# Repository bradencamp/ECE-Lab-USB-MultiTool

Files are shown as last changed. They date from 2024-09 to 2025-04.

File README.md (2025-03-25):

# ECE-Lab-USB-Multitool
In recent years students have been required to purchase USB Laboratory Instruments such as the Analog Discovery 2 (AD2) from Digilent Inc or the Advanced Active Learning Module (ADALM 2000) from Analog Devices. These devices allow the students to complete Laboratory exercises at home and to experiment on their own time without the need to rely on open lab hours. The COVID pandemic created a high demand for such devices as throughout the US lab classes have been converted to at-home labs. This high demand in concert with the chip crises has propelled the price for these devices to currently $199 and $249 (academic price for the AD2 and AD3 respectively) and $237 (ADALM2000).

This USB Multi-function Laboratory Instrument will be inexpensive and therefore less capable than the AD2 or ADALM 2000 while still fulfilling the requirements for most laboratory exercises in the undergraduate ECE curriculum. This new device should use a microcontroller with analog front ends for the Oscilloscope and Wave Form Generator functionality. It should function as a 2 channel Oscilloscope and Arbitrary Waveform Generator (AWG) with a Bandwidth of up to 2 MHz and a sample rate of 5 Msps, a 16 channel logic analyzer, and be controllable via USB from a PC (Windows, Mac, and Linux) as well as offering live waveform viewing on a PC. The total part cost should not exceed $50. A similar project was once offered by the Opencope MZ (https://digilent.com/reference/test-and-measurement/openscope-mz/start) which has been discontinued.

Previous senior design projects have built a one-channel prototype for of the oscilloscope and a two channel AWG. However, the oscilloscope did not fully meet the requirements. The arbitrary waveform generator function is complete. The logic analyzer is now a separate project and currently being designed. The goal of this project is to learn from the oscilloscope prototype and create one that meets the requirements and integrate the arbitrary waveform generator and the logic analyzer, all with an intuitive and easy to use graphical user interface on the PC using PyQtGraph. This project requires analog circuit design of amplifiers, filters, etc., while being cost-conscious. The fewer different parts are needed and the fewer parts are needed overall, the more likely you'll meet the $50 target. It also requires programming of an STM-32 microcontroller in C, GUI design and programming in Python.

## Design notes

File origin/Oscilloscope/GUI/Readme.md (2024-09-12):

# Python libraries needed
- time
- Pyserial
- Serial
- PyQt5
- NumPy
- PyQtGraph
# Instructions

- For the GUI to run, the port and baudrate number needs to match the MCU's serial. 
- The board also needs to be connected for it to work.
- To change the port and baudrate number, change reader = SerialReader(port='COM7', baudrate=12000000) in line 400 of the code.
- COM7 can be changed to COM# depending on the port number in the Device Manager of Windows.
- The main function "def update():" is the main loop that collects the data and plots it.

# Improvments to the code

- Implementing the "time" function as the code is getting the ADC data can be used to set a time function that goes to the x-axis.

- using NumPy's FFT function can be used to show the frequincy number being generated.

- Creating an automatic COM port detector to remove the need of updating it for each new device.

What can suffice is using this example:
```python
	com_number, ok = QtGui.QInputDialog.getText(None, "COM Port", "Enter COM#:")
	if ok:
		ser = serial.Serial(f"COM{com_number}", 12000000)
	else:
		print("Wrong COM port, exiting...")
		exit()
```
This  will prompt a window to input the COM# before opining the GUI.

# FIXME
- add trigger function.

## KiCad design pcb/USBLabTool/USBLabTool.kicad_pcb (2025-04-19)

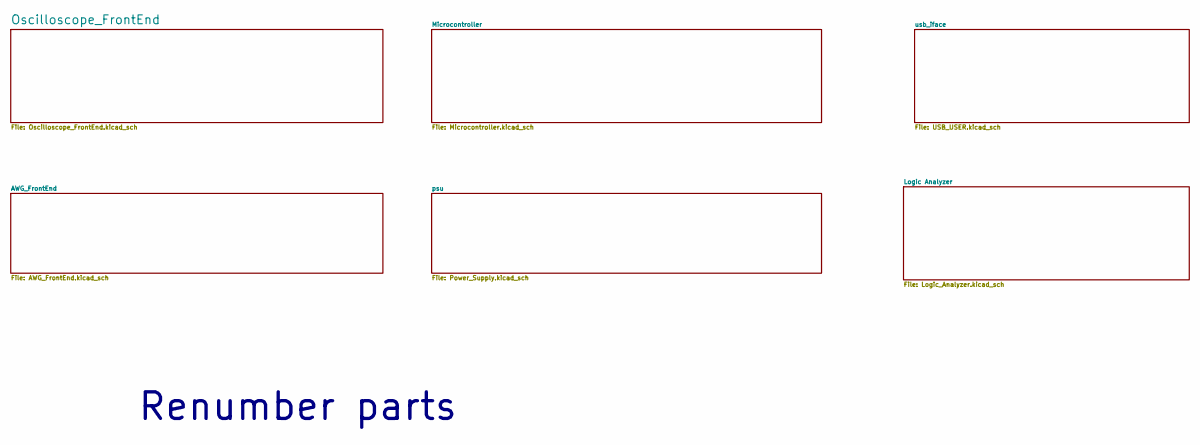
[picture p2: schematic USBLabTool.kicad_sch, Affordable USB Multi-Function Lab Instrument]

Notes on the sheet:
Renumber parts

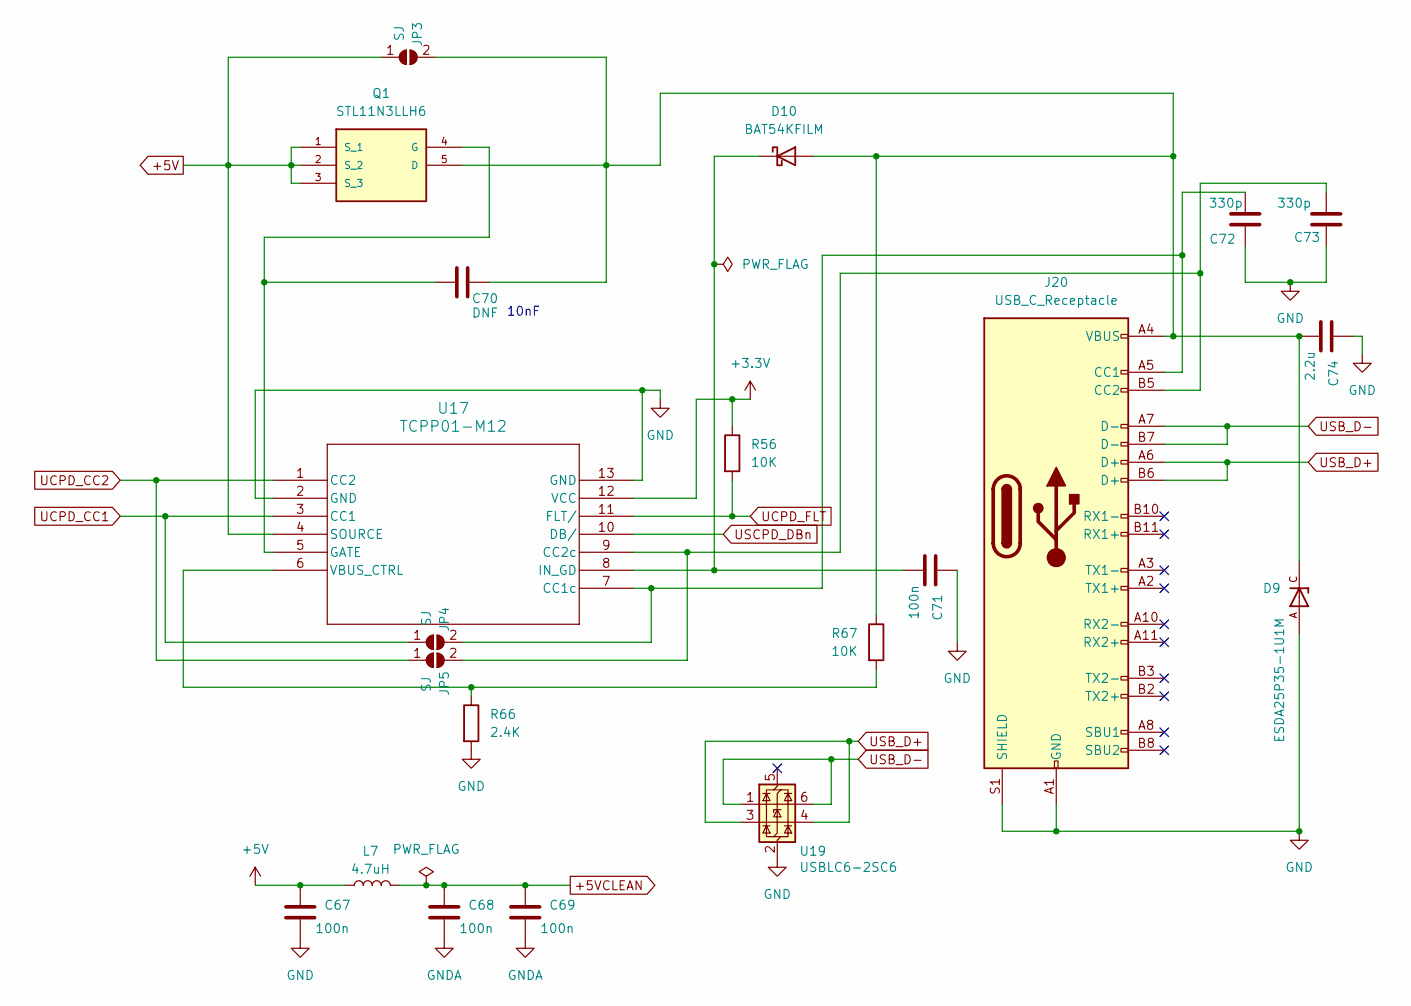
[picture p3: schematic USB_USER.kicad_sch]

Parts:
C67, C68, C69, C71: 100n; C_0603_1608Metric_Pad1.08x0.95mm_HandSolder
C70: DNF; C_0603_1608Metric_Pad1.08x0.95mm_HandSolder
C72, C73: 330p; C_0201_0603Metric_Pad0.64x0.40mm_HandSolder
C74: 2.2u; C_0603_1608Metric_Pad1.08x0.95mm_HandSolder
D9: ESDA25P35-1U1M; TVS_ESDA25P35-1U1M; PARTREV 2
D10: BAT54KFILM; D_SOD-523
J20: USB_C_Receptacle; USB_C_Receptacle_Amphenol_12401610E4-2A
JP3, JP4, JP5: SJ; SolderJumper-2_P1.3mm_Open_RoundedPad1.0x1.5mm
L7: 4.7uH; L_0603_1608Metric_Pad1.05x0.95mm_HandSolder; Mouser REF 80-L0603B470KPWFT
Q1: STL11N3LLH6; STL20N6F7; MANUFACTURER_PART_NUMBER STL11N3LLH6; DigiKey_Part_Number 497-11099-2-ND
R56, R67: 10K; R_0603_1608Metric
R66: 2.4K; R_0603_1608Metric
U17: TCPP01-M12; QFN12_TCPP01-M12_STM
U19: USBLC6-2SC6; SOT-23-6

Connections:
+3.3V: R56.1, U17.12 (VCC); also elsewhere on the board
+5V: C67.1, JP3.1 (A), L7.1, Q1.1 (S_1), Q1.2 (S_2), Q1.3 (S_3), U17.4 (SOURCE); also elsewhere on the board
+5VCLEAN: C68.1, C69.1, L7.2; also elsewhere on the board
GND: C67.2, C71.1, C72.1, C73.1, C74.1, D9.A, J20.A1 (GND), J20.A12 (GND), J20.B1 (GND), J20.B12 (GND), J20.S1 (SHIELD), R66.2, U17.2 (GND), U17.13 (GND), U19.2 (GND); also elsewhere on the board
GNDA: C68.2, C69.2; also elsewhere on the board
unnamed: C70.1, C74.2, D9.C, D10.2 (A), J20.A4 (VBUS), J20.A9 (VBUS), J20.B4 (VBUS), J20.B9 (VBUS), JP3.2 (B), Q1.5 (D), R67.1
unnamed: C71.2, D10.1 (K), U17.8 (IN_GD)
unnamed: C72.2, J20.A5 (CC1), JP4.2 (B), U17.7 (CC1c)
unnamed: C73.2, J20.B5 (CC2), JP5.2 (B), U17.9 (CC2c)
unnamed: C70.2, Q1.4 (G), U17.5 (GATE)
unnamed: R66.1, R67.2, U17.6 (VBUS_CTRL)
UCPD_CC1: JP4.1 (A), U17.3 (CC1); also elsewhere on the board
UCPD_CC2: JP5.1 (A), U17.1 (CC2); also elsewhere on the board
UCPD_FLT: R56.2, U17.11 (FLT/); also elsewhere on the board
USB_D+: J20.A6 (D+), J20.B6 (D+), U19.3 (I/O2), U19.4 (I/O2); also elsewhere on the board
USB_D-: J20.A7 (D-), J20.B7 (D-), U19.1 (I/O1), U19.6 (I/O1); also elsewhere on the board
USCPD_DBn: U17.10 (DB/); also elsewhere on the board

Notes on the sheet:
10nF

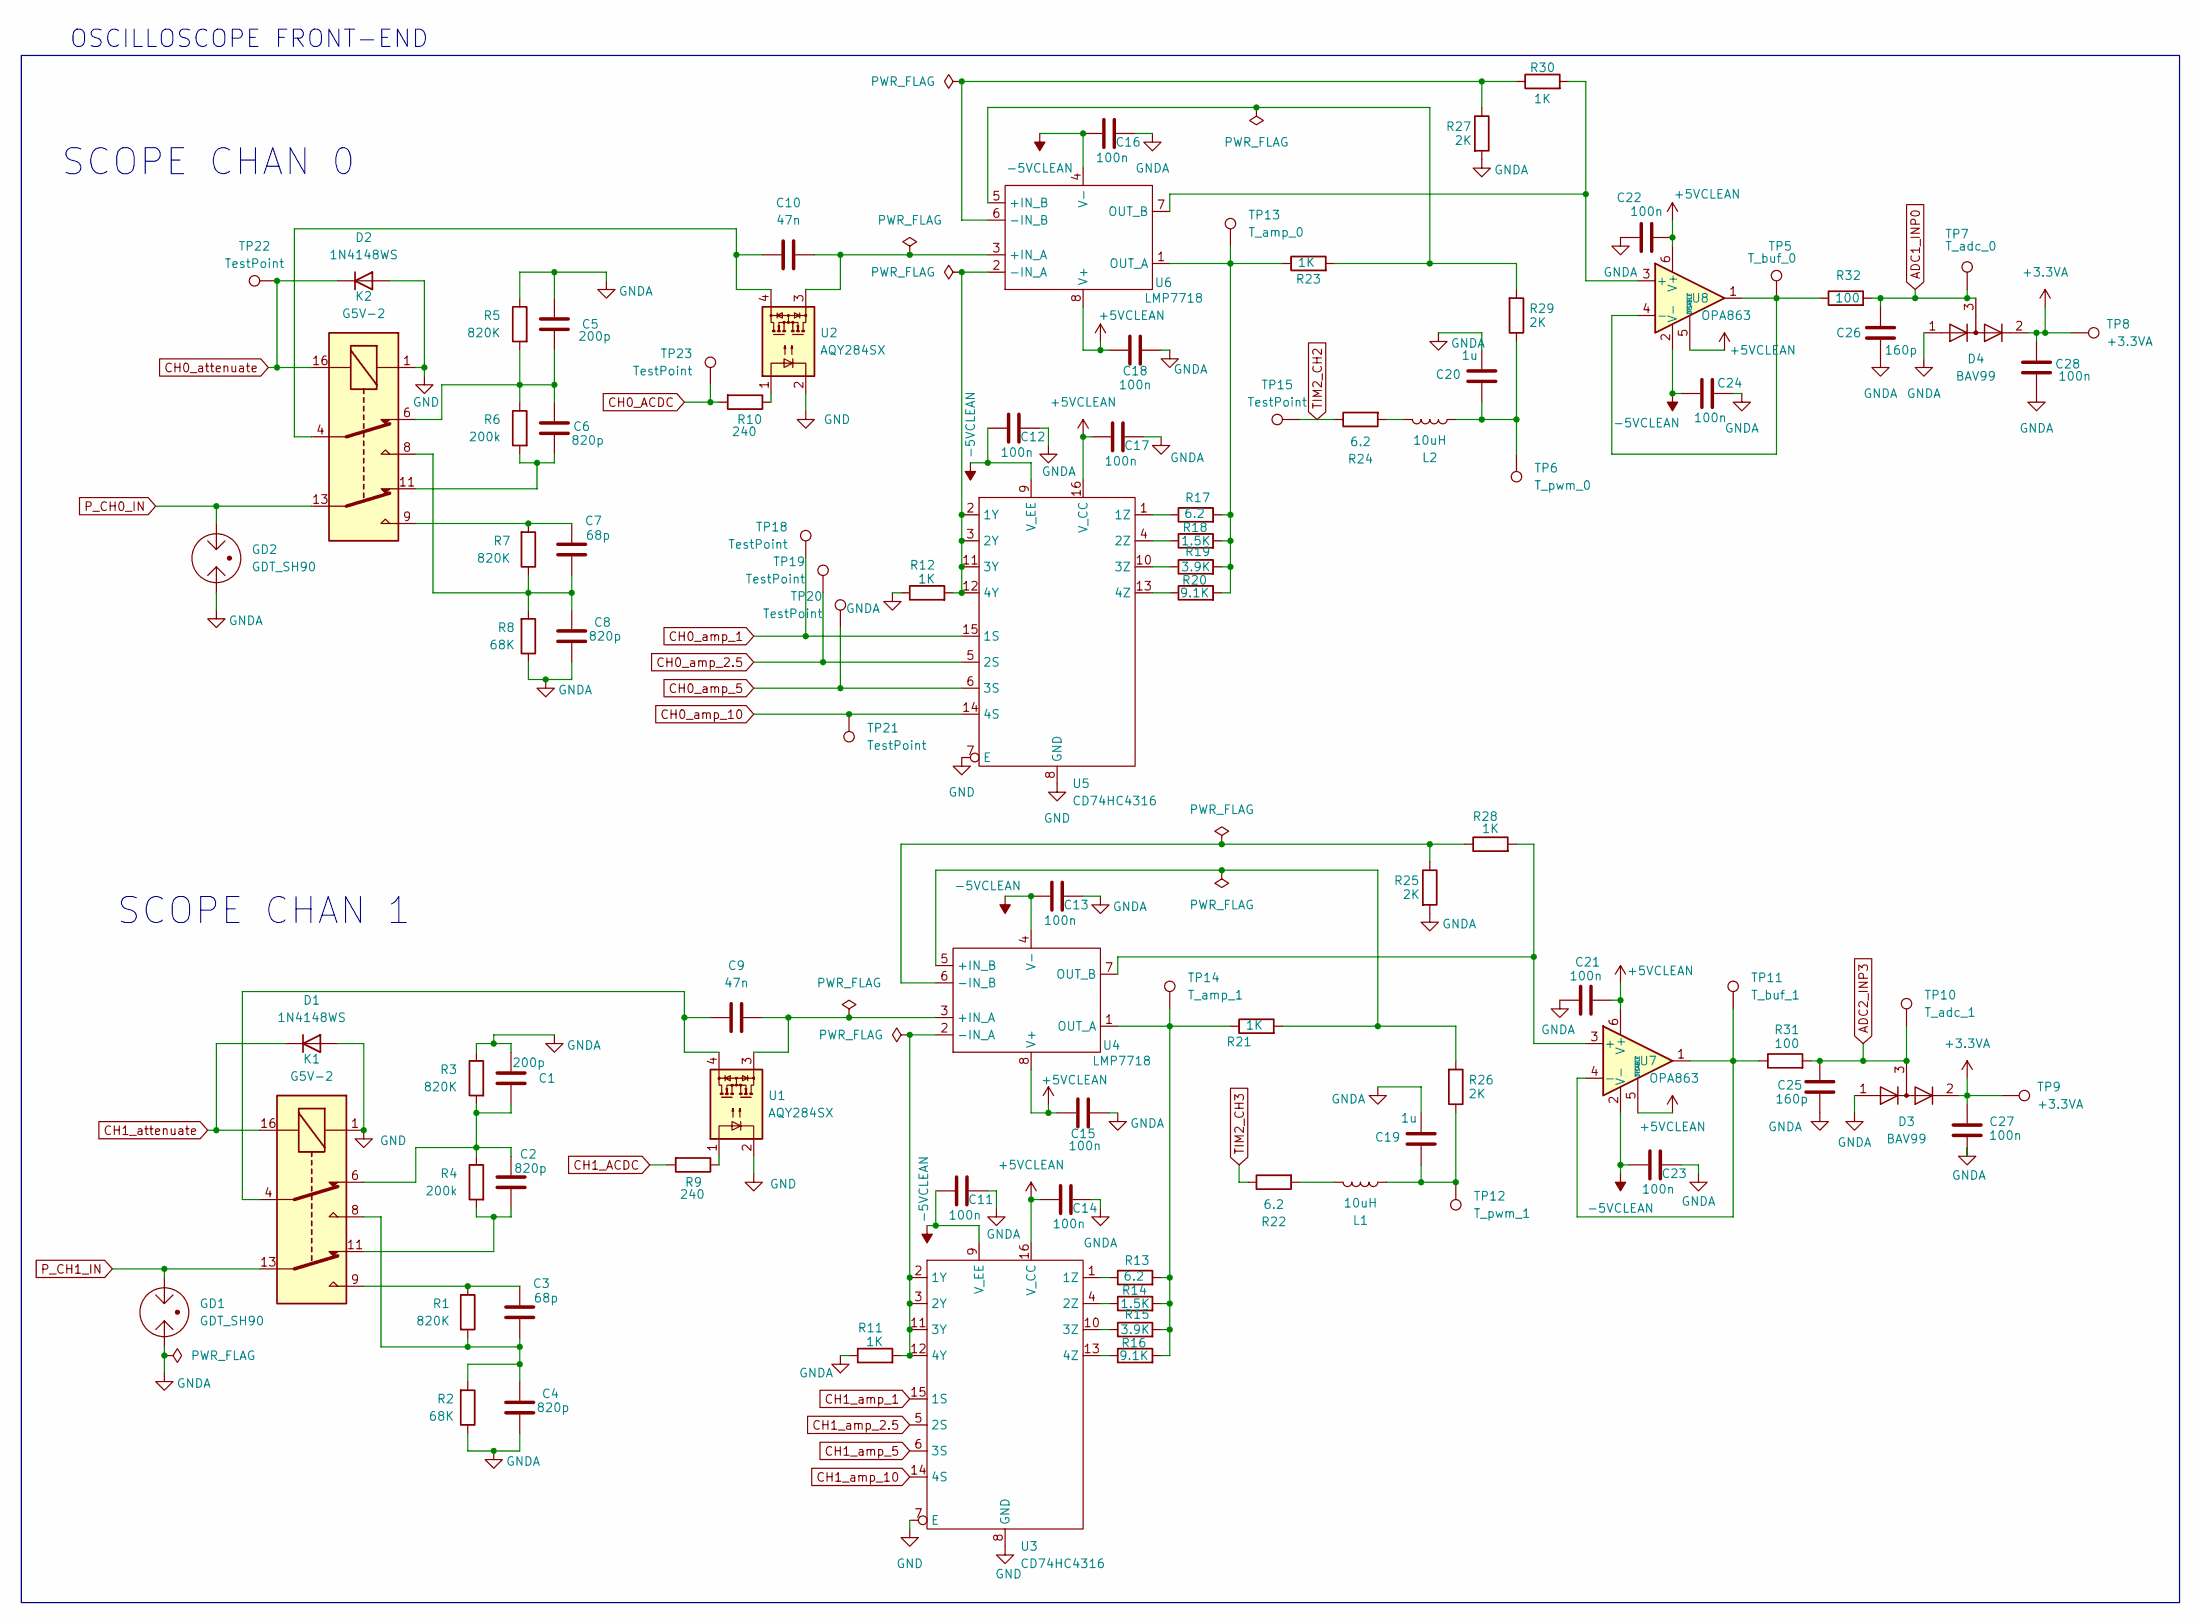
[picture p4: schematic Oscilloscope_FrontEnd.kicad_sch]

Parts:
C1, C5: 200p; C_0603_1608Metric_Pad1.08x0.95mm_HandSolder
C2, C4, C6, C8: 820p; C_0603_1608Metric_Pad1.08x0.95mm_HandSolder
C3, C7: 68p; C_0603_1608Metric_Pad1.08x0.95mm_HandSolder
C9, C10: 47n; C_0603_1608Metric_Pad1.08x0.95mm_HandSolder
C11, C12, C13, C14, C15, C16, C17, C18, C21, C22, C23, C24, C27, C28: 100n; C_0603_1608Metric_Pad1.08x0.95mm_HandSolder
C19, C20: 1u; C_0603_1608Metric_Pad1.08x0.95mm_HandSolder
C25, C26: 160p; C_0603_1608Metric_Pad1.08x0.95mm_HandSolder
D1, D2: 1N4148WS; D_SOD-323
D3, D4: BAV99; SOT-23
GD1, GD2: GDT_SH90; GDT_SH_LTF
K1, K2: G5V-2; Relay_DPDT_Omron_G5V-2
L1, L2: 10uH; L_0603_1608Metric_Pad1.05x0.95mm_HandSolder
R1, R3, R5, R7: 820K; R_0603_1608Metric_Pad0.98x0.95mm_HandSolder
R2, R8: 68K; R_0603_1608Metric_Pad0.98x0.95mm_HandSolder
R4, R6: 200k; R_0603_1608Metric_Pad0.98x0.95mm_HandSolder
R9, R10: 240; R_0603_1608Metric_Pad0.98x0.95mm_HandSolder
R11, R12, R21, R23, R28, R30: 1K; R_0603_1608Metric_Pad0.98x0.95mm_HandSolder
R13, R17, R22, R24: 6.2; R_0603_1608Metric_Pad0.98x0.95mm_HandSolder
R14, R18: 1.5K; R_0603_1608Metric_Pad0.98x0.95mm_HandSolder
R15, R19: 3.9K; R_0603_1608Metric_Pad0.98x0.95mm_HandSolder
R16, R20: 9.1K; R_0603_1608Metric_Pad0.98x0.95mm_HandSolder
R25, R26, R27, R29: 2K; R_0603_1608Metric_Pad0.98x0.95mm_HandSolder
R31, R32: 100; R_0603_1608Metric_Pad0.98x0.95mm_HandSolder
TP5: T_buf_0; TestPoint_Pad_D2.0mm
TP6: T_pwm_0; TestPoint_Pad_D2.0mm
TP7: T_adc_0; TestPoint_Pad_2.0x2.0mm
TP8, TP9: +3.3VA; TestPoint_Pad_D2.0mm
TP10: T_adc_1; TestPoint_Pad_D2.0mm
TP11: T_buf_1; TestPoint_Pad_D2.0mm
TP12: T_pwm_1; TestPoint_Pad_D2.0mm
TP13: T_amp_0; TestPoint_Pad_D2.0mm
TP14: T_amp_1; TestPoint_Pad_D2.0mm
TP15, TP18, TP19, TP20, TP21, TP22, TP23: TestPoint; TestPoint_Pad_2.0x2.0mm
U1, U2: AQY284SX; SOP-4_3.8x4.1mm_P2.54mm
U3, U5: CD74HC4316; TSSOP-16_4.4x5mm_P0.65mm
U4, U6: LMP7718; VSSOP-8_3x3mm_P0.65mm
U7, U8: OPA863; SOT-23-6_Handsoldering

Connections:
+3.3VA: C27.1, C28.1, D3.2 (A), D4.2 (A), TP8.1, TP9.1; also elsewhere on the board
+5VCLEAN: C14.1, C15.1, C17.1, C18.1, C21.2, C22.2, U3.16 (V_CC), U4.8 (V+), U5.16 (V_CC), U6.8 (V+), U7.5 (~DISABLE), U7.6 (V+), U8.5 (~DISABLE), U8.6 (V+); also elsewhere on the board
-5VCLEAN: C11.1, C12.1, C13.1, C16.1, C23.1, C24.1, U3.9 (V_EE), U4.4 (V-), U5.9 (V_EE), U6.4 (V-), U7.2 (V-), U8.2 (V-); also elsewhere on the board
ADC1_INP0: C26.1, D4.3 (K), R32.2, TP7.1; also elsewhere on the board
ADC2_INP3: C25.1, D3.3 (K), R31.2, TP10.1; also elsewhere on the board
CH0_ACDC: R10.2, TP23.1; also elsewhere on the board
CH0_amp_1: TP18.1, U5.15 (1S); also elsewhere on the board
CH0_amp_2.5: TP19.1, U5.5 (2S); also elsewhere on the board
CH0_amp_5: TP20.1, U5.6 (3S); also elsewhere on the board
CH0_amp_10: TP21.1, U5.14 (4S); also elsewhere on the board
CH0_attenuate: D2.1 (K), K2.16, TP22.1; also elsewhere on the board
CH1_ACDC: R9.2; also elsewhere on the board
CH1_amp_1: U3.15 (1S); also elsewhere on the board
CH1_amp_2.5: U3.5 (2S); also elsewhere on the board
CH1_amp_5: U3.6 (3S); also elsewhere on the board
CH1_amp_10: U3.14 (4S); also elsewhere on the board
CH1_attenuate: D1.1 (K), K1.16; also elsewhere on the board
GND: D1.2 (A), D2.2 (A), K1.1, K2.1, U1.2, U2.2, U3.7 (E), U3.8 (GND), U5.7 (E), U5.8 (GND); also elsewhere on the board
GNDA: C1.1, C4.2, C5.1, C8.2, C11.2, C12.2, C13.2, C14.2, C15.2, C16.2, C17.2, C18.2, C19.2, C20.2, C21.1, C22.1, C23.2, C24.2, C25.2, C26.2, C27.2, C28.2, D3.1 (K), D4.1 (K), GD1.1, GD2.1, R2.1, R3.1, R5.1, R8.1, R11.1, R12.1, R25.2, R27.2; also elsewhere on the board
unnamed: C1.2, C2.1, K1.6, R3.2, R4.1
unnamed: C2.2, K1.11, R4.2
unnamed: C3.1, K1.9, R1.2
unnamed: C3.2, C4.1, K1.8, R1.1, R2.2
unnamed: C5.2, C6.1, K2.6, R5.2, R6.1
unnamed: C6.2, K2.11, R6.2
unnamed: C7.1, K2.9, R7.2
unnamed: C7.2, C8.1, K2.8, R7.1, R8.2
unnamed: C9.1, K1.4, U1.4
unnamed: C10.1, K2.4, U2.4
unnamed: C19.1, L1.2, R26.1, TP12.1
unnamed: C20.1, L2.2, R29.1, TP6.1
unnamed: L1.1, R22.2
unnamed: L2.1, R24.2
unnamed: R9.1, U1.1
unnamed: R10.1, U2.1
unnamed: R11.2, U3.2 (1Y), U3.3 (2Y), U3.11 (3Y), U3.12 (4Y), U4.2 (-IN_A)
unnamed: R13.1, U3.1 (1Z)
unnamed: R14.1, U3.4 (2Z)
unnamed: R15.1, U3.10 (3Z)
unnamed: R16.1, U3.13 (4Z)
unnamed: C9.2, U1.3, U4.3 (+IN_A)
unnamed: R21.2, R26.2, U4.5 (+IN_B)
unnamed: R25.1, R28.1, U4.6 (-IN_B)
unnamed: R13.2, R14.2, R15.2, R16.2, R21.1, TP14.1, U4.1 (OUT_A)
unnamed: R28.2, U4.7 (OUT_B), U7.3 (+)
unnamed: R12.2, U5.2 (1Y), U5.3 (2Y), U5.11 (3Y), U5.12 (4Y), U6.2 (-IN_A)
unnamed: R17.1, U5.1 (1Z)
unnamed: R18.1, U5.4 (2Z)
unnamed: R19.1, U5.10 (3Z)
unnamed: R20.1, U5.13 (4Z)
unnamed: C10.2, U2.3, U6.3 (+IN_A)
unnamed: R23.2, R29.2, U6.5 (+IN_B)
unnamed: R27.1, R30.1, U6.6 (-IN_B)
unnamed: R17.2, R18.2, R19.2, R20.2, R23.1, TP13.1, U6.1 (OUT_A)
unnamed: R30.2, U6.7 (OUT_B), U8.3 (+)
unnamed: R31.1, TP11.1, U7.1, U7.4 (-)
unnamed: R32.1, TP5.1, U8.1, U8.4 (-)
P_CH0_IN: GD2.2, K2.13; also elsewhere on the board
P_CH1_IN: GD1.2, K1.13; also elsewhere on the board
TIM2_CH2: R24.1, TP15.1; also elsewhere on the board
TIM2_CH3: R22.1; also elsewhere on the board

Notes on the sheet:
OSCILLOSCOPE FRONT-END
SCOPE CHAN 0
SCOPE CHAN 1

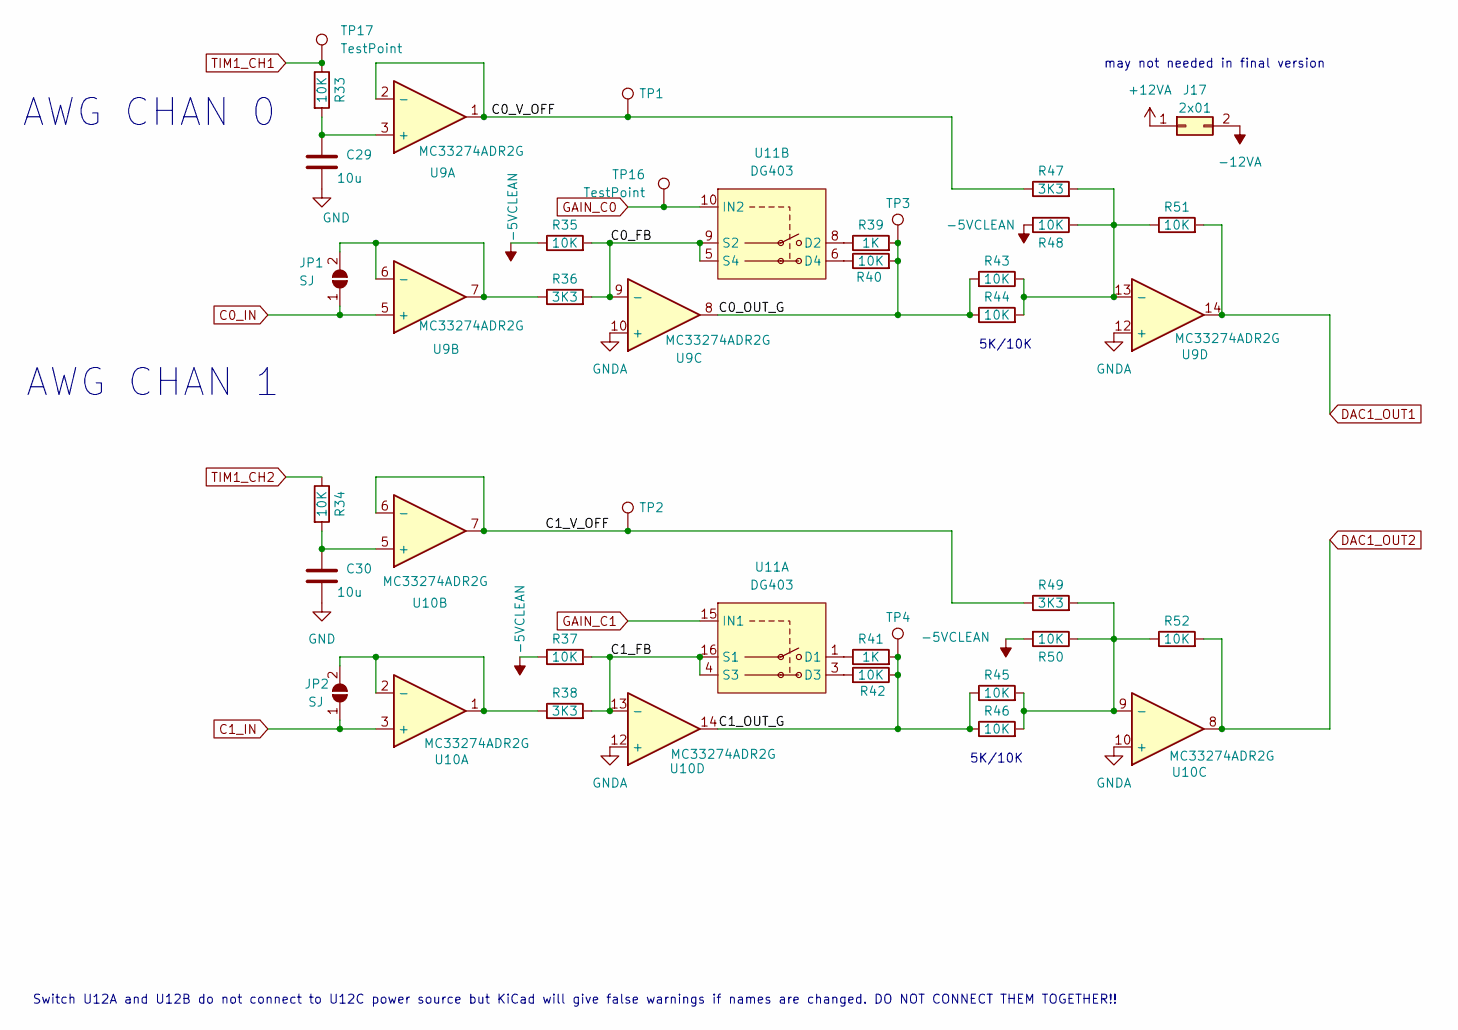
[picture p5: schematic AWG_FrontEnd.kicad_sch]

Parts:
C29, C30: 10u; C_0805_2012Metric_Pad1.18x1.45mm_HandSolder
J17: 2x01; PinHeader_2x01_P2.54mm_Vertical
JP1, JP2: SJ; SolderJumper-2_P1.3mm_Open_RoundedPad1.0x1.5mm
R33, R34, R35, R37, R40, R42, R43, R44, R45, R46, R48, R50, R51, R52: 10K; R_0603_1608Metric
R36, R38, R47, R49: 3K3; R_0603_1608Metric
R39, R41: 1K; R_0603_1608Metric
TP1, TP2, TP3, TP4: TestPoint; TestPoint_Pad_D2.0mm
TP16, TP17: TestPoint; TestPoint_Pad_2.0x2.0mm
U9, U10: MC33274ADR2G; SOIC-14_3.9x8.7mm_P1.27mm
U11: DG403; TSSOP-16_4.4x5mm_P0.65mm

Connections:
+12VA: J17.1; also elsewhere on the board
-5VCLEAN: R35.1, R37.1, R48.2, R50.2; also elsewhere on the board
-12VA: J17.2; also elsewhere on the board
/AWG_FrontEnd/C0_FB: R35.2, R36.2, U9.9 (-), U11.5 (S4), U11.9 (S2)
/AWG_FrontEnd/C0_OUT_G: R39.2, R40.2, R43.2, R44.1, TP3.1, U9.8
/AWG_FrontEnd/C0_V_OFF: R47.1, TP1.1, U9.1, U9.2 (-)
/AWG_FrontEnd/C1_FB: R37.2, R38.2, U10.13 (-), U11.4 (S3), U11.16 (S1)
/AWG_FrontEnd/C1_OUT_G: R41.2, R42.1, R45.1, R46.1, TP4.1, U10.14
/AWG_FrontEnd/C1_V_OFF: R49.1, TP2.1, U10.6 (-), U10.7
C0_IN: JP1.1 (A), U9.5 (+); also elsewhere on the board
C1_IN: JP2.1 (A), U10.3 (+); also elsewhere on the board
DAC1_OUT1: R51.2, U9.14; also elsewhere on the board
DAC1_OUT2: R52.2, U10.8; also elsewhere on the board
GAIN_C0: TP16.1, U11.10 (IN2); also elsewhere on the board
GAIN_C1: U11.15 (IN1); also elsewhere on the board
GND: C29.2, C30.2; also elsewhere on the board
GNDA: U9.10 (+), U9.12 (+), U10.10 (+), U10.12 (+); also elsewhere on the board
unnamed: JP1.2 (B), R36.1, U9.6 (-), U9.7
unnamed: JP2.2 (B), R38.1, U10.1, U10.2 (-)
unnamed: C29.1, R33.2, U9.3 (+)
unnamed: R43.1, R44.2, R47.2, R48.1, R51.1, U9.13 (-)
unnamed: C30.1, R34.2, U10.5 (+)
unnamed: R45.2, R46.2, R49.2, R50.1, R52.1, U10.9 (-)
unnamed: R41.1, U11.1 (D1)
unnamed: R42.2, U11.3 (D3)
unnamed: R39.1, U11.8 (D2)
unnamed: R40.1, U11.6 (D4)
TIM1_CH1: R33.1, TP17.1; also elsewhere on the board
TIM1_CH2: R34.1; also elsewhere on the board

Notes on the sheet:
AWG CHAN 0
AWG CHAN 1
5K/10K
Switch U12A and U12B do not connect to U12C power source but KiCad will give false warnings if names are changed. DO NOT CONNECT THEM TOGETHER!!
may not needed in final version

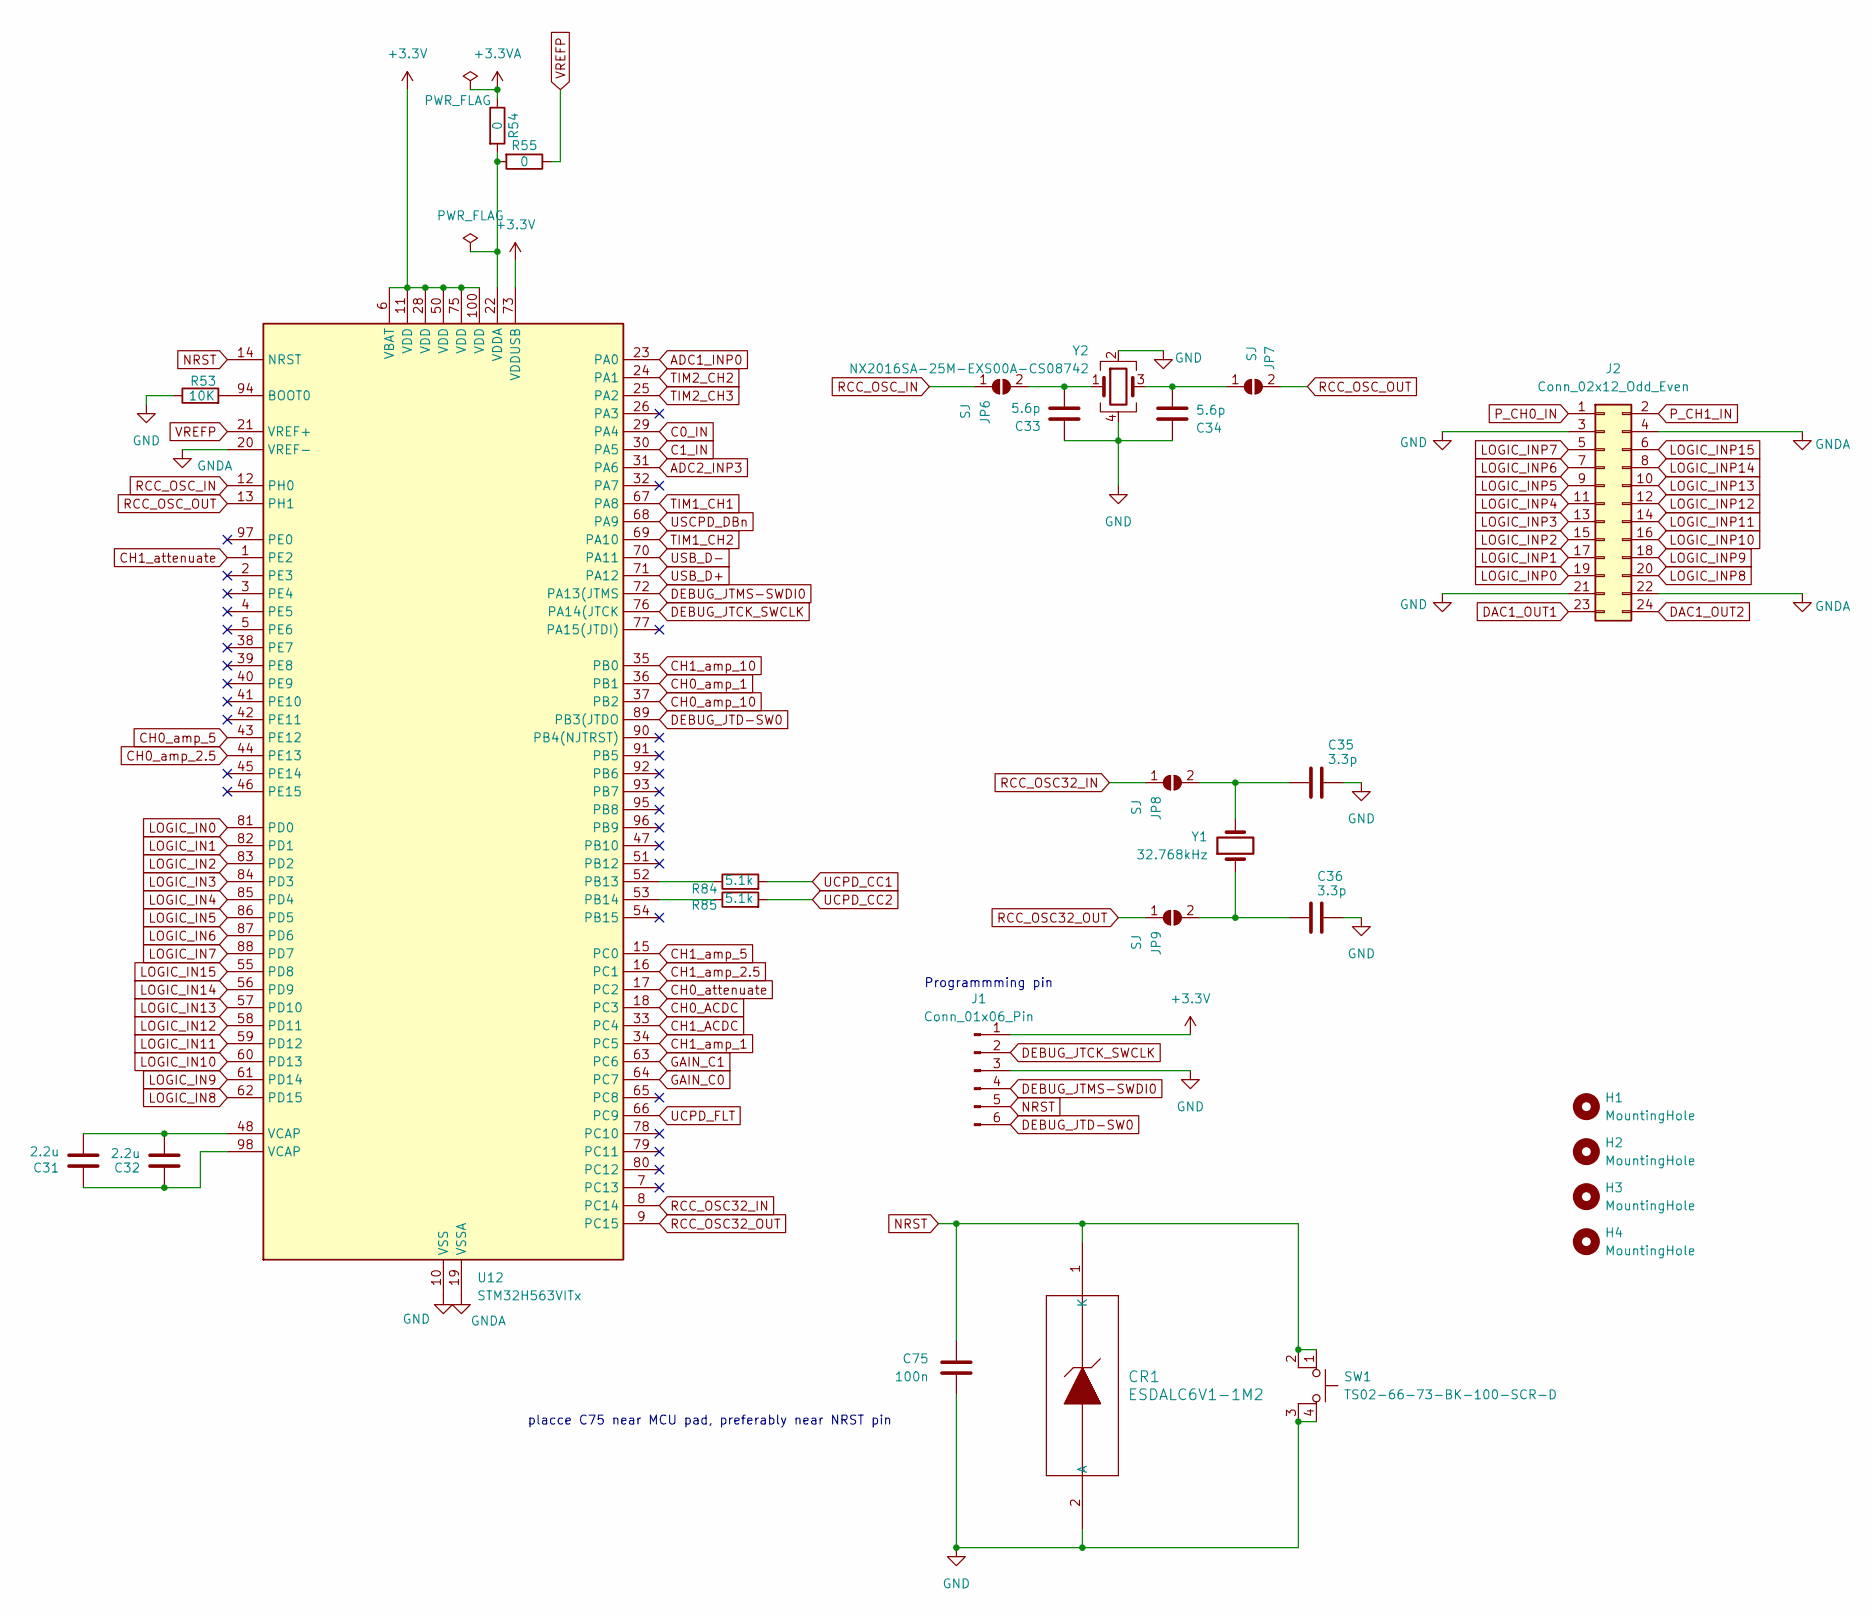
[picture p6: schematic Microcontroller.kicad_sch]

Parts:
C31, C32: 2.2u; D_0805_2012Metric_Pad1.15x1.40mm_HandSolder
C33, C34: 5.6p; C_0201_0603Metric_Pad0.64x0.40mm_HandSolder
C35, C36: 3.3p; C_0201_0603Metric_Pad0.64x0.40mm_HandSolder
C75: 100n; C_0603_1608Metric_Pad1.08x0.95mm_HandSolder
CR1: ESDALC6V1-1M2; D_SOD-882
H1, H2, H3, H4: MountingHole; MountingHole_2.2mm_M2
J1: Conn_01x06_Pin; PinHeader_1x06_P2.54mm_Vertical
J2: Conn_02x12_Odd_Even; OST_302-R241
JP6, JP7, JP8, JP9: SJ; SolderJumper-2_P1.3mm_Open_RoundedPad1.0x1.5mm
R53: 10K; R_0603_1608Metric
R54, R55: 0; R_0603_1608Metric_Pad0.98x0.95mm_HandSolder
R84, R85: 5.1k; R_0603_1608Metric_Pad0.98x0.95mm_HandSolder
SW1: TS02-66-73-BK-100-SCR-D; SW_TS02-66-73-BK-100-SCR-D
U12: STM32H563VITx; LQFP-100_14x14mm_P0.5mm
Y1: 32.768kHz; Crystal_SMD_MicroCrystal_CC7V-T1A-2Pin_3.2x1.5mm_HandSolder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
Y2: NX2016SA-25M-EXS00A-CS08742; NX2016SA_NDK

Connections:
+3.3V: J1.1, U12.6 (VBAT), U12.11 (VDD), U12.28 (VDD), U12.50 (VDD), U12.73 (VDDUSB), U12.75 (VDD), U12.100 (VDD); also elsewhere on the board
+3.3VA: R54.1; also elsewhere on the board
ADC1_INP0: U12.23 (PA0); also elsewhere on the board
ADC2_INP3: U12.31 (PA6); also elsewhere on the board
C0_IN: U12.29 (PA4); also elsewhere on the board
C1_IN: U12.30 (PA5); also elsewhere on the board
CH0_ACDC: U12.18 (PC3); also elsewhere on the board
CH0_amp_1: U12.36 (PB1); also elsewhere on the board
CH0_amp_2.5: U12.44 (PE13); also elsewhere on the board
CH0_amp_5: U12.43 (PE12); also elsewhere on the board
CH0_amp_10: U12.37 (PB2); also elsewhere on the board
CH0_attenuate: U12.17 (PC2); also elsewhere on the board
CH1_ACDC: U12.33 (PC4); also elsewhere on the board
CH1_amp_1: U12.34 (PC5); also elsewhere on the board
CH1_amp_2.5: U12.16 (PC1); also elsewhere on the board
CH1_amp_5: U12.15 (PC0); also elsewhere on the board
CH1_amp_10: U12.35 (PB0); also elsewhere on the board
CH1_attenuate: U12.1 (PE2); also elsewhere on the board
DAC1_OUT1: J2.23; also elsewhere on the board
DAC1_OUT2: J2.24; also elsewhere on the board
DEBUG_JTCK_SWCLK: J1.2, U12.76 (PA14(JTCK)
DEBUG_JTD-SW0: J1.6, U12.89 (PB3(JTDO)
DEBUG_JTMS-SWDI0: J1.4, U12.72 (PA13(JTMS)
GAIN_C0: U12.64 (PC7); also elsewhere on the board
GAIN_C1: U12.63 (PC6); also elsewhere on the board
GND: C33.2, C34.1, C35.1, C36.1, C75.2, CR1.2 (A), J1.3, J2.3, J2.21, R53.1, SW1.3 (K), SW1.4 (A), U12.10 (VSS), U12.27 (VSS), U12.49 (VSS), U12.74 (VSS), U12.99 (VSS), Y2.2, Y2.4; also elsewhere on the board
GNDA: J2.4, J2.22, U12.19 (VSSA), U12.20 (VREF-); also elsewhere on the board
LOGIC_IN0: U12.81 (PD0); also elsewhere on the board
LOGIC_IN1: U12.82 (PD1); also elsewhere on the board
LOGIC_IN2: U12.83 (PD2); also elsewhere on the board
LOGIC_IN3: U12.84 (PD3); also elsewhere on the board
LOGIC_IN4: U12.85 (PD4); also elsewhere on the board
LOGIC_IN5: U12.86 (PD5); also elsewhere on the board
LOGIC_IN6: U12.87 (PD6); also elsewhere on the board
LOGIC_IN7: U12.88 (PD7); also elsewhere on the board
LOGIC_IN8: U12.62 (PD15); also elsewhere on the board
LOGIC_IN9: U12.61 (PD14); also elsewhere on the board
LOGIC_IN10: U12.60 (PD13); also elsewhere on the board
LOGIC_IN11: U12.59 (PD12); also elsewhere on the board
LOGIC_IN12: U12.58 (PD11); also elsewhere on the board
LOGIC_IN13: U12.57 (PD10); also elsewhere on the board
LOGIC_IN14: U12.56 (PD9); also elsewhere on the board
LOGIC_IN15: U12.55 (PD8); also elsewhere on the board
LOGIC_INP0: J2.19; also elsewhere on the board
LOGIC_INP1: J2.17; also elsewhere on the board
LOGIC_INP2: J2.15; also elsewhere on the board
LOGIC_INP3: J2.13; also elsewhere on the board
LOGIC_INP4: J2.11; also elsewhere on the board
LOGIC_INP5: J2.9; also elsewhere on the board
LOGIC_INP6: J2.7; also elsewhere on the board
LOGIC_INP7: J2.5; also elsewhere on the board
LOGIC_INP8: J2.20; also elsewhere on the board
LOGIC_INP9: J2.18; also elsewhere on the board
LOGIC_INP10: J2.16; also elsewhere on the board
LOGIC_INP11: J2.14; also elsewhere on the board
LOGIC_INP12: J2.12; also elsewhere on the board
LOGIC_INP13: J2.10; also elsewhere on the board
LOGIC_INP14: J2.8; also elsewhere on the board
LOGIC_INP15: J2.6; also elsewhere on the board
NRST: C75.1, CR1.1 (K), J1.5, SW1.1, SW1.2, U12.14 (NRST)
unnamed: C31.1, C32.1, U12.98 (VCAP)
unnamed: C31.2, C32.2, U12.48 (VCAP)
unnamed: C33.1, JP6.2 (B), Y2.1
unnamed: C34.2, JP7.1 (A), Y2.3
unnamed: C35.2, JP8.2 (B), Y1.2
unnamed: C36.2, JP9.2 (B), Y1.1
unnamed: R53.2, U12.94 (BOOT0)
unnamed: R84.1, U12.52 (PB13)
unnamed: R85.1, U12.53 (PB14)
unnamed: R54.2, R55.2, U12.22 (VDDA)
P_CH0_IN: J2.1; also elsewhere on the board
P_CH1_IN: J2.2; also elsewhere on the board
RCC_OSC32_IN: JP8.1 (A), U12.8 (PC14)
RCC_OSC32_OUT: JP9.1 (A), U12.9 (PC15)
RCC_OSC_IN: JP6.1 (A), U12.12 (PH0)
RCC_OSC_OUT: JP7.2 (B), U12.13 (PH1)
TIM1_CH1: U12.67 (PA8); also elsewhere on the board
TIM1_CH2: U12.69 (PA10); also elsewhere on the board
TIM2_CH2: U12.24 (PA1); also elsewhere on the board
TIM2_CH3: U12.25 (PA2); also elsewhere on the board
UCPD_CC1: R84.2; also elsewhere on the board
UCPD_CC2: R85.2; also elsewhere on the board
UCPD_FLT: U12.66 (PC9); also elsewhere on the board
USB_D+: U12.71 (PA12); also elsewhere on the board
USB_D-: U12.70 (PA11); also elsewhere on the board
USCPD_DBn: U12.68 (PA9); also elsewhere on the board
VREFP: R55.1, U12.21 (VREF+)

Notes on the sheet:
placce C75 near MCU pad, preferably near NRST pin
Programmming pin

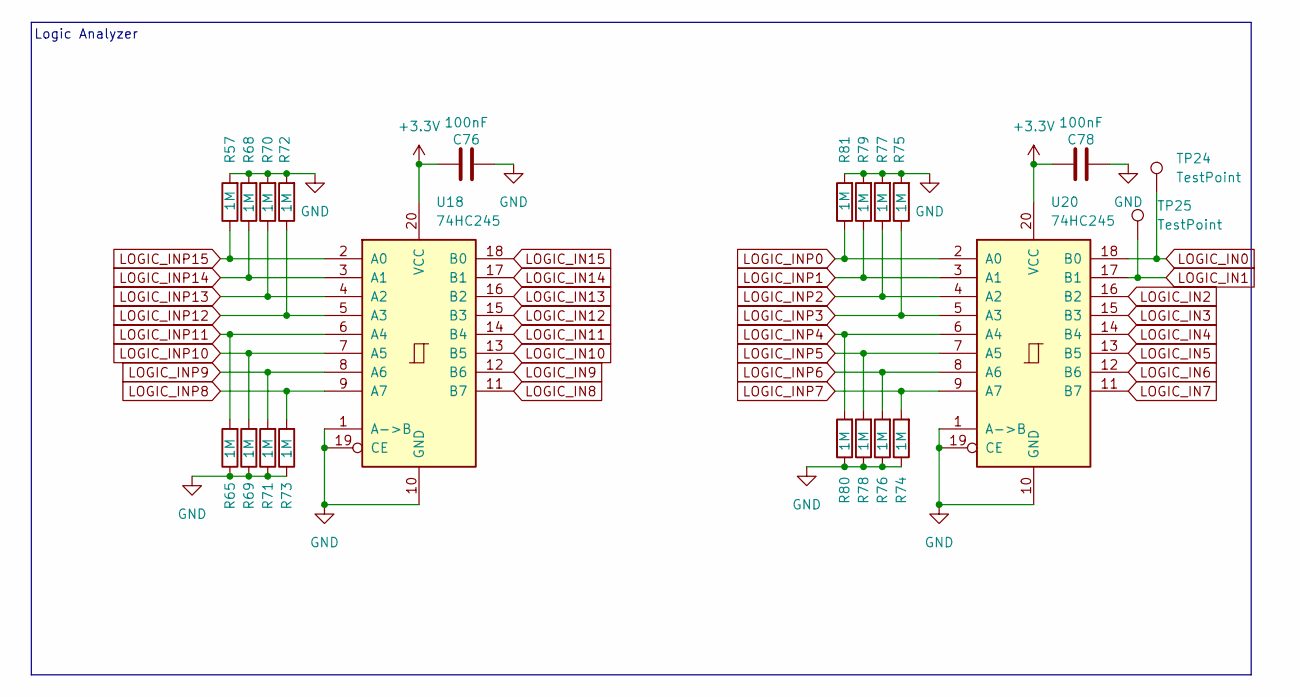
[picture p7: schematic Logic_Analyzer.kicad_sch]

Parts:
C76, C78: 100nF; C_0603_1608Metric
R57, R65, R68, R69, R70, R71, R72, R73, R74, R75, R76, R77, R78, R79, R80, R81: 1M; R_0603_1608Metric
TP24, TP25: TestPoint; TestPoint_Pad_2.0x2.0mm
U18, U20: 74HC245; DHVQFN-20-1EP_2.5x4.5mm_P0.5mm_EP1x3mm

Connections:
+3.3V: C76.1, C78.1, U18.20 (VCC), U20.20 (VCC); also elsewhere on the board
GND: C76.2, C78.2, R57.2, R65.1, R68.2, R69.1, R70.2, R71.1, R72.2, R73.1, R74.1, R75.2, R76.1, R77.2, R78.1, R79.2, R80.1, R81.2, U18.1 (A->B), U18.10 (GND), U18.19 (CE), U20.1 (A->B), U20.10 (GND), U20.19 (CE); also elsewhere on the board
LOGIC_IN0: TP24.1, U20.18 (B0); also elsewhere on the board
LOGIC_IN1: TP25.1, U20.17 (B1); also elsewhere on the board
LOGIC_IN2: U20.16 (B2); also elsewhere on the board
LOGIC_IN3: U20.15 (B3); also elsewhere on the board
LOGIC_IN4: U20.14 (B4); also elsewhere on the board
LOGIC_IN5: U20.13 (B5); also elsewhere on the board
LOGIC_IN6: U20.12 (B6); also elsewhere on the board
LOGIC_IN7: U20.11 (B7); also elsewhere on the board
LOGIC_IN8: U18.11 (B7); also elsewhere on the board
LOGIC_IN9: U18.12 (B6); also elsewhere on the board
LOGIC_IN10: U18.13 (B5); also elsewhere on the board
LOGIC_IN11: U18.14 (B4); also elsewhere on the board
LOGIC_IN12: U18.15 (B3); also elsewhere on the board
LOGIC_IN13: U18.16 (B2); also elsewhere on the board
LOGIC_IN14: U18.17 (B1); also elsewhere on the board
LOGIC_IN15: U18.18 (B0); also elsewhere on the board
LOGIC_INP0: R81.1, U20.2 (A0); also elsewhere on the board
LOGIC_INP1: R79.1, U20.3 (A1); also elsewhere on the board
LOGIC_INP2: R77.1, U20.4 (A2); also elsewhere on the board
LOGIC_INP3: R75.1, U20.5 (A3); also elsewhere on the board
LOGIC_INP4: R80.2, U20.6 (A4); also elsewhere on the board
LOGIC_INP5: R78.2, U20.7 (A5); also elsewhere on the board
LOGIC_INP6: R76.2, U20.8 (A6); also elsewhere on the board
LOGIC_INP7: R74.2, U20.9 (A7); also elsewhere on the board
LOGIC_INP8: R73.2, U18.9 (A7); also elsewhere on the board
LOGIC_INP9: R71.2, U18.8 (A6); also elsewhere on the board
LOGIC_INP10: R69.2, U18.7 (A5); also elsewhere on the board
LOGIC_INP11: R65.2, U18.6 (A4); also elsewhere on the board
LOGIC_INP12: R72.1, U18.5 (A3); also elsewhere on the board
LOGIC_INP13: R70.1, U18.4 (A2); also elsewhere on the board
LOGIC_INP14: R68.1, U18.3 (A1); also elsewhere on the board
LOGIC_INP15: R57.1, U18.2 (A0); also elsewhere on the board

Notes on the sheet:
Logic Analyzer

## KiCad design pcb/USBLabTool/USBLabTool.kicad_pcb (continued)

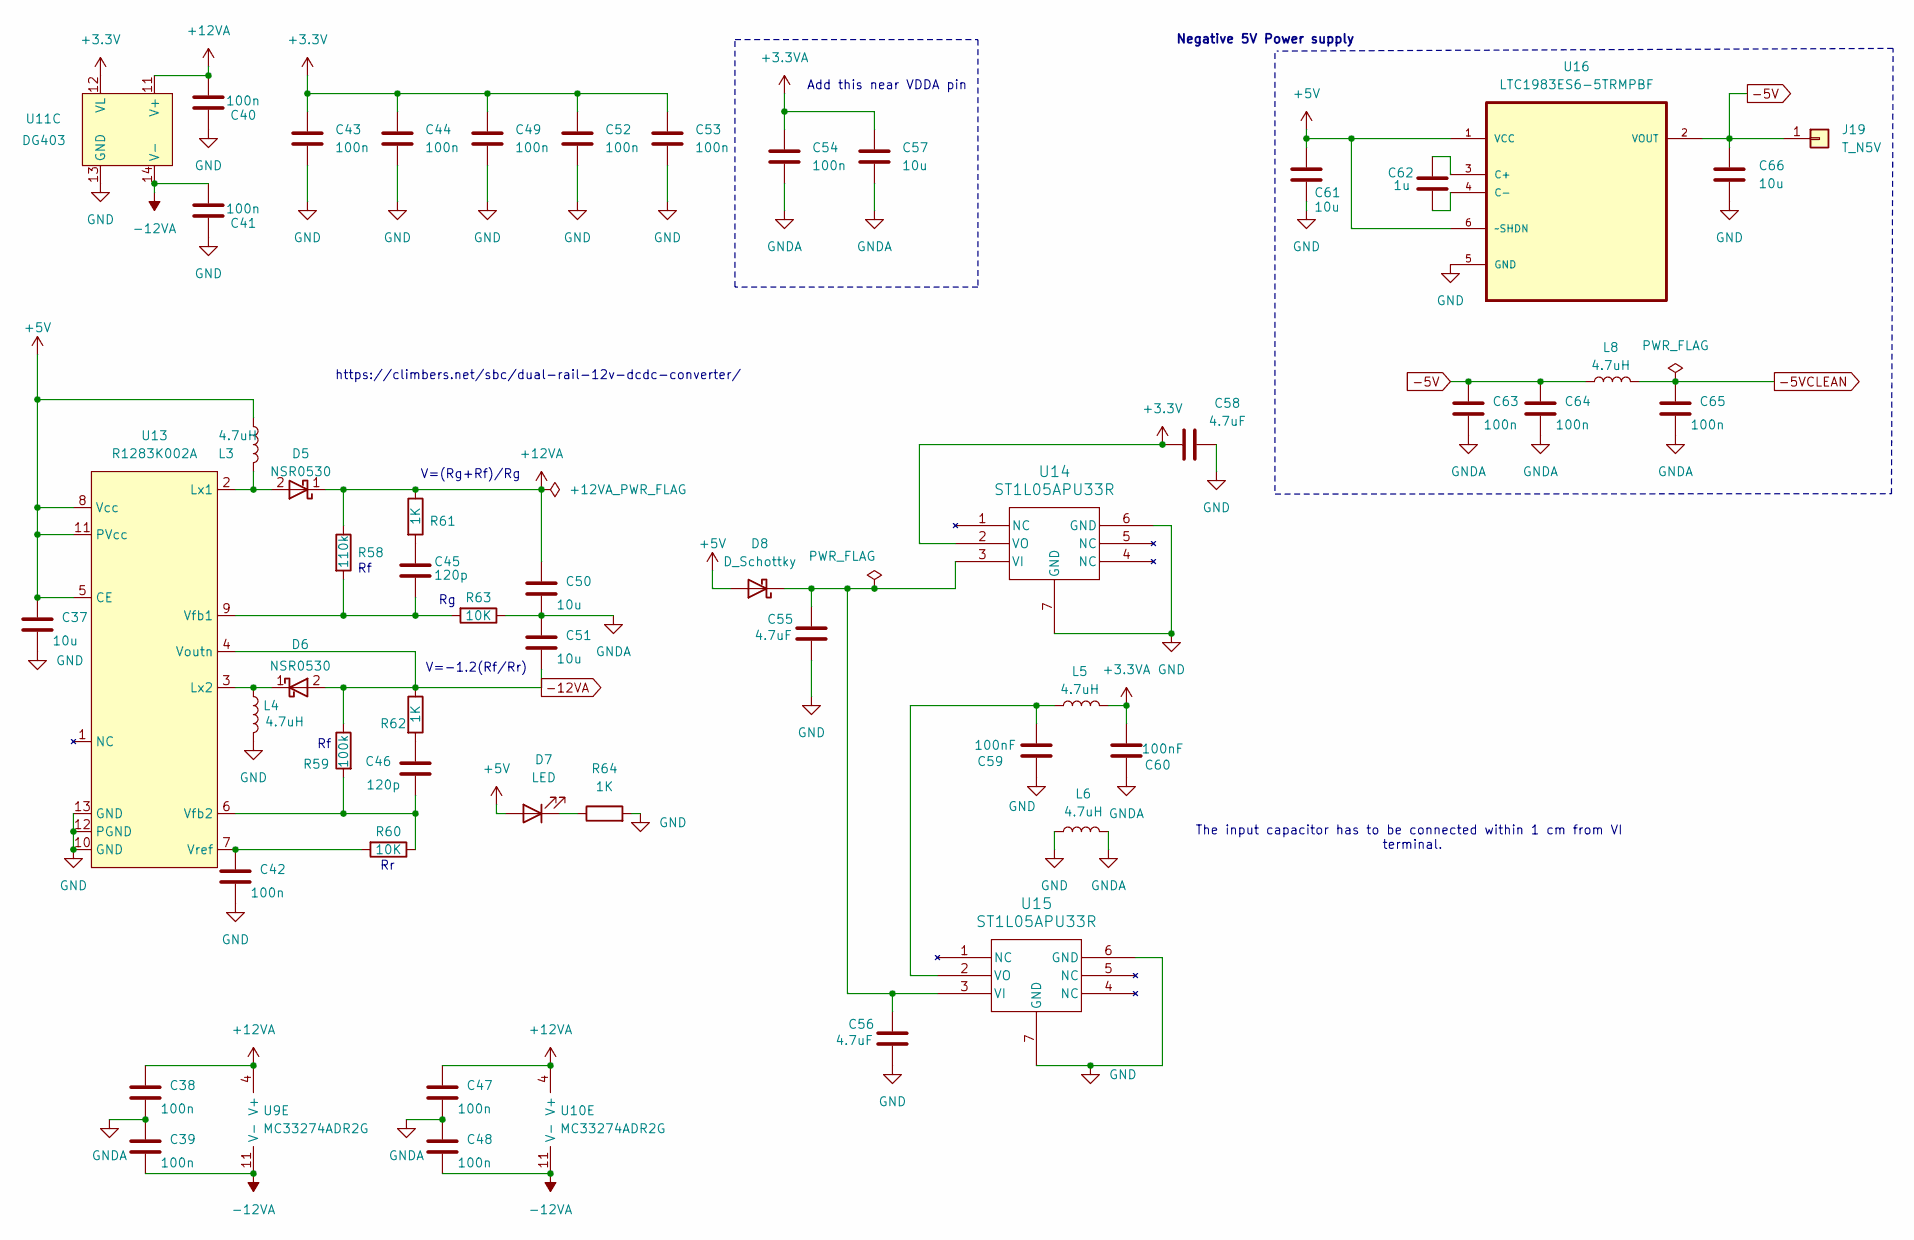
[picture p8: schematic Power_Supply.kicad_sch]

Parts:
C37, C50, C51: 10u; C_0805_2012Metric_Pad1.18x1.45mm_HandSolder
C38, C39, C40, C41, C43, C44, C47, C48, C49, C52, C53, C54, C63, C64, C65: 100n; C_0603_1608Metric_Pad1.08x0.95mm_HandSolder
C42: 100n; C_0201_0603Metric_Pad0.64x0.40mm_HandSolder
C45, C46: 120p; C_0603_1608Metric_Pad1.08x0.95mm_HandSolder
C55, C56, C58: 4.7uF; C_0603_1608Metric_Pad1.08x0.95mm_HandSolder
C57, C61, C66: 10u; C_0603_1608Metric_Pad1.08x0.95mm_HandSolder
C59, C60: 100nF; C_0603_1608Metric_Pad1.08x0.95mm_HandSolder
C62: 1u; C_0603_1608Metric_Pad1.08x0.95mm_HandSolder
D5, D6: NSR0530; D_SOD-323_HandSoldering
D7: LED; LED_D5.0mm
D8: D_Schottky; D_1206_3216Metric_Pad1.42x1.75mm_HandSolder; Mouser REF 512-SS24FL
J19: T_N5V; PinHeader_1x01_P2.54mm_Vertical
L3, L4: 4.7uH; IND_TAIYO_NRH2410_TAY
L5, L6: 4.7uH; IND_TAIYO_NRH2410_TAY; Mouser REF 80-L0603B470KPWFT
L8: 4.7uH; L_0603_1608Metric_Pad1.05x0.95mm_HandSolder; Mouser REF 80-L0603B470KPWFT
R58: 110k; R_0603_1608Metric
R59: 100k; R_0603_1608Metric
R60, R63: 10K; R_0603_1608Metric
R61, R62, R64: 1K; R_0603_1608Metric
U9, U10: MC33274ADR2G; SOIC-14_3.9x8.7mm_P1.27mm
U11: DG403; TSSOP-16_4.4x5mm_P0.65mm
U13: R1283K002A; ST_UFDFPN-12-1EP_3x3mm_P0.5mm_EP1.4x2.55mm
U14, U15: ST1L05APU33R; DFN_5APU33R_STM
U16: LTC1983ES6-5TRMPBF; TSOT-23-6_HandSoldering; MPN LTC1983ES6-5#TRMPBF

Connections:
+3.3V: C43.1, C44.1, C49.1, C52.1, C53.1, C58.2, U11.12 (VL), U14.2 (VO); also elsewhere on the board
+3.3VA: C54.1, C57.1, C60.2, L5.2; also elsewhere on the board
+5V: C37.1, C61.1, D7.2 (A), D8.2 (A), L3.1, U13.5 (CE), U13.8 (Vcc), U13.11 (PVcc), U16.1 (VCC), U16.6 (~SHDN); also elsewhere on the board
+12VA: C38.1, C40.2, C47.1, C50.1, D5.1 (K), R58.1, R61.1, U9.4 (V+), U10.4 (V+), U11.11 (V+); also elsewhere on the board
-5V: C63.1, C64.1, C66.1, J19.1, L8.1, U16.2 (VOUT)
-5VCLEAN: C65.1, L8.2; also elsewhere on the board
-12VA: C39.2, C41.2, C48.2, C51.2, D6.2 (A), R59.1, R62.1, U9.11 (V-), U10.11 (V-), U11.14 (V-), U13.4 (Voutn); also elsewhere on the board
GND: C37.2, C40.1, C41.1, C42.2, C43.2, C44.2, C49.2, C52.2, C53.2, C55.2, C56.2, C58.1, C59.1, C61.2, C66.2, L4.2, L6.1, R64.2, U11.13 (GND), U13.10 (GND), U13.12 (PGND), U13.13 (GND), U14.6 (GND), U14.7 (GND), U15.6 (GND), U15.7 (GND), U16.5 (GND); also elsewhere on the board
GNDA: C38.2, C39.1, C47.2, C48.1, C50.2, C51.1, C54.2, C57.2, C60.1, C63.2, C64.2, C65.2, L6.2, R63.1; also elsewhere on the board
unnamed: C45.1, R61.2
unnamed: C46.1, R62.2
unnamed: D5.2 (A), L3.2, U13.2 (Lx1)
unnamed: D6.1 (K), L4.1, U13.3 (Lx2)
unnamed: D7.1 (K), R64.1
unnamed: C55.1, C56.1, D8.1 (K), U14.3 (VI), U15.3 (VI)
unnamed: C45.2, R58.2, R63.2, U13.9 (Vfb1)
unnamed: C46.2, R59.2, R60.1, U13.6 (Vfb2)
unnamed: C42.1, R60.2, U13.7 (Vref)
unnamed: C59.2, L5.1, U15.2 (VO)
unnamed: C62.1, U16.3 (C+)
unnamed: C62.2, U16.4 (C-)

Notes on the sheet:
The input capacitor has to be connected within 1 cm from VI terminal.
https://climbers.net/sbc/dual-rail-12v-dcdc-converter/
Add this near VDDA pin
V=(Rg+Rf)/Rg
V=-1.2(Rf/Rr)
Negative 5V Power supply

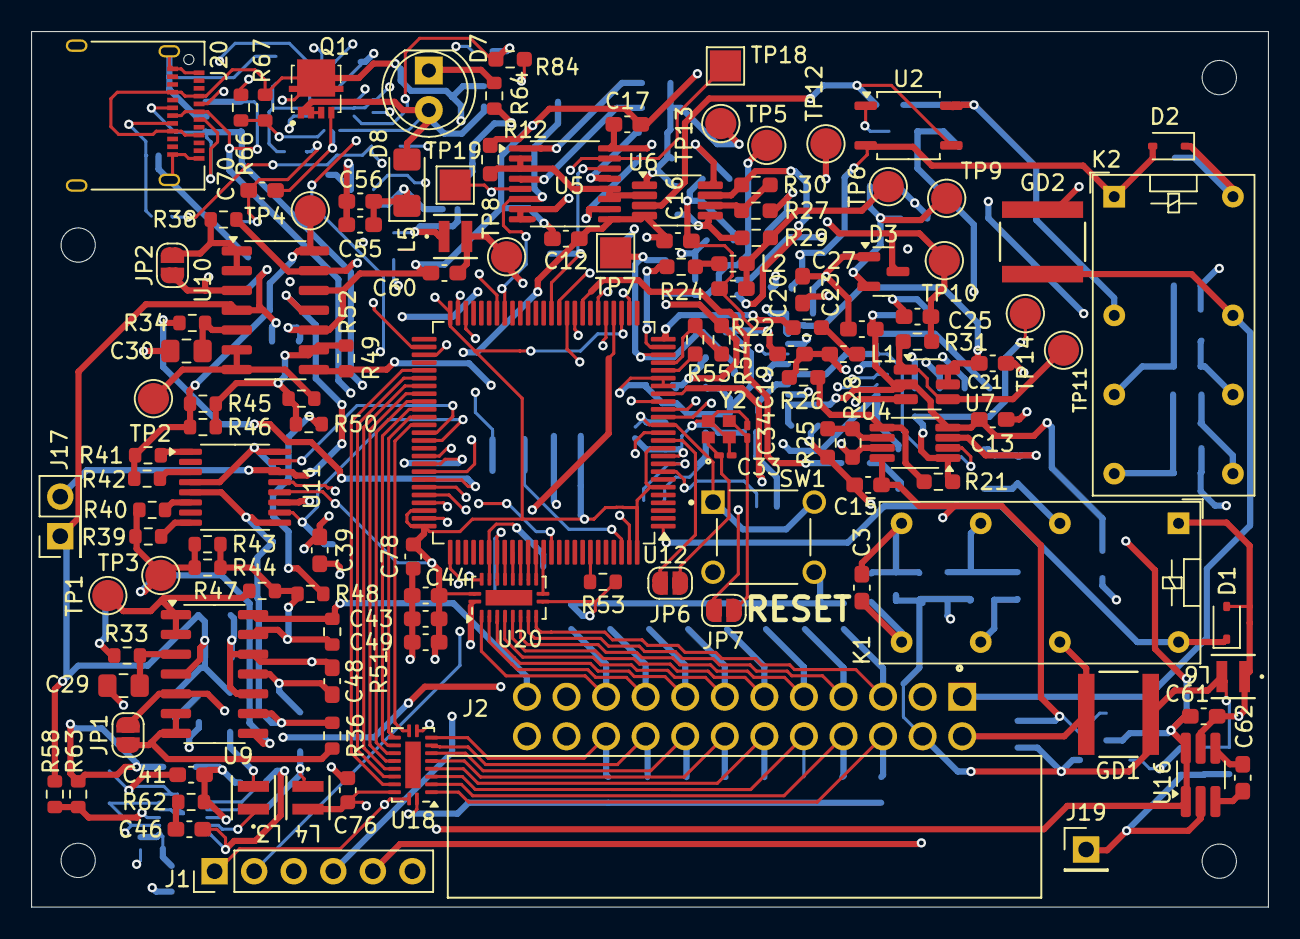
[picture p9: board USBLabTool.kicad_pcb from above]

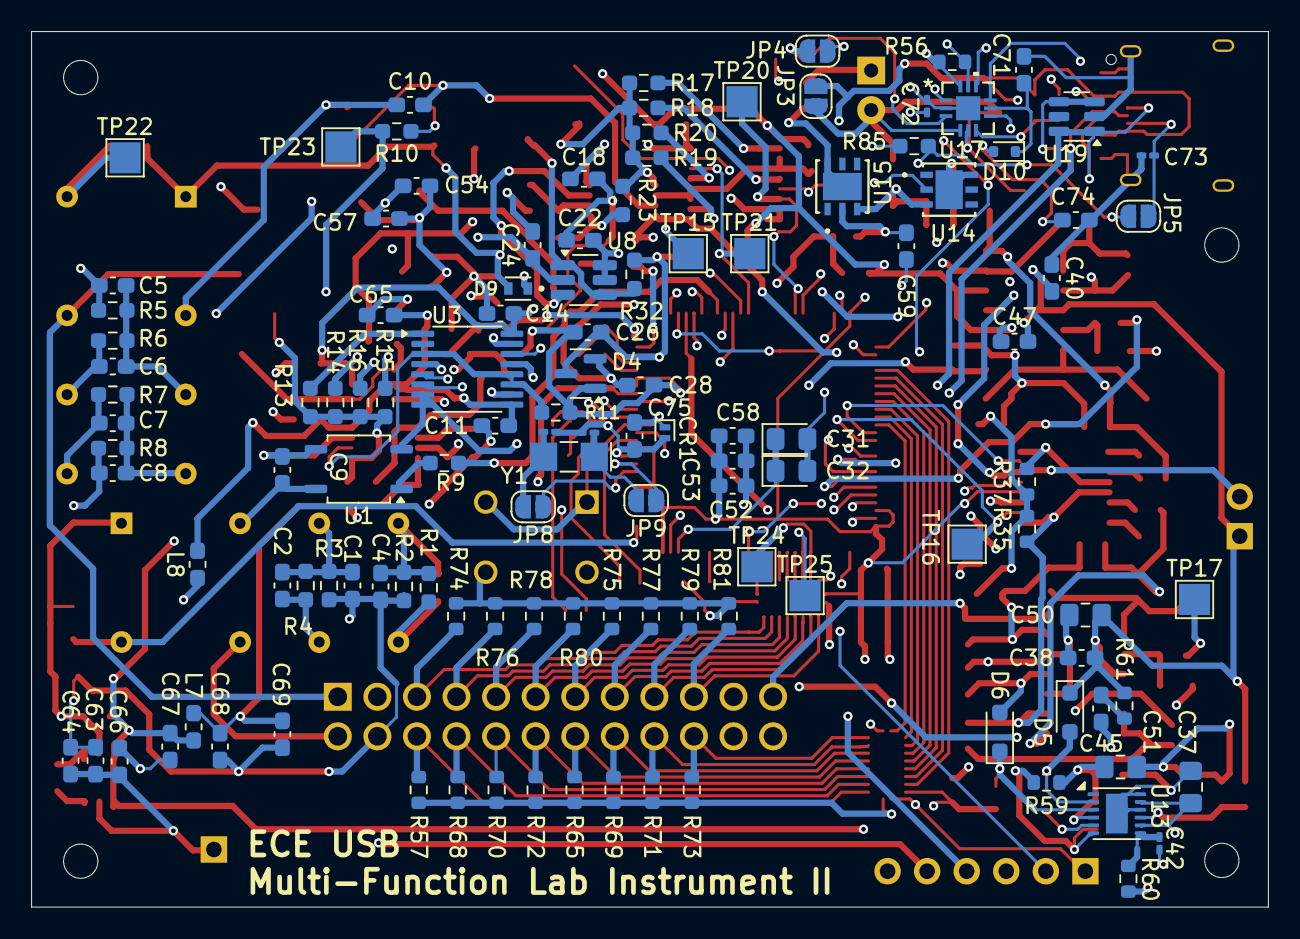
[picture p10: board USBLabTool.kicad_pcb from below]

Board: 4 copper layers, 79.4 x 56.2 mm, 250 parts (121 on the bottom side), 165 nets.

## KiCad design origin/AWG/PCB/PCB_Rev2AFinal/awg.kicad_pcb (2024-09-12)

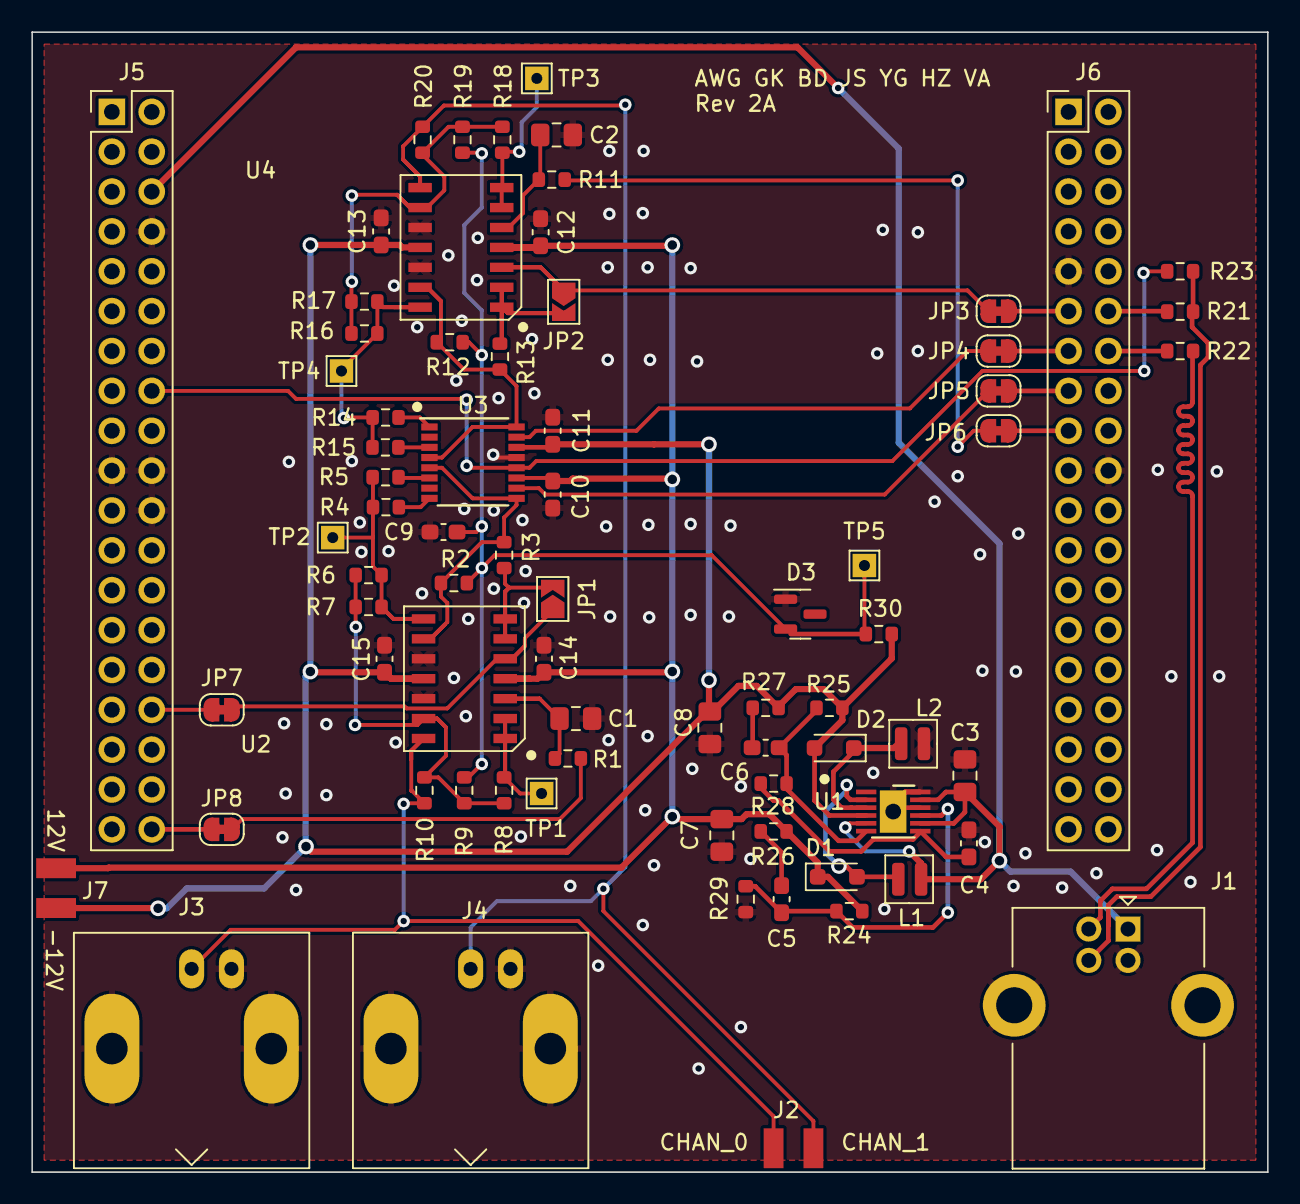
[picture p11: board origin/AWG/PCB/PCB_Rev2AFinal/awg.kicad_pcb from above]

Board: 2 copper layers, 78.7 x 72.6 mm, 74 parts (0 on the bottom side), 47 nets.

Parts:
C1, C2, C3, C7, C8: 10u; C_0805_2012Metric_Pad1.18x1.45mm_HandSolder
C4, C9, C10, C11, C12, C13, C14, C15: 100n; C_0603_1608Metric_Pad1.08x0.95mm_HandSolder
C5, C6: 120p; C_0603_1608Metric_Pad1.08x0.95mm_HandSolder
D1, D2: NSR0530; D_SOD-323_HandSoldering
D3: LM4040-5; SOT-23
J1: USB_B; USB_B_Lumberg_2411_02_Horizontal
J2: 02x02; 2x02
J3, J4: BNC; BNC_Amphenol_B6252HB-NPP3G-50_Horizontal
J5: nuc303_LEFT; PinHeader_2x19_P2.54mm_Vertical
J6: nuc303_RIGHT; PinHeader_2x19_P2.54mm_Vertical
J7: 2x01; 1x02
JP1, JP2: SJ; SolderJumper-2_P1.3mm_Open_TrianglePad1.0x1.5mm
JP3, JP4, JP5, JP6, JP7, JP8: JP; SolderJumper-2_P1.3mm_Bridged_RoundedPad1.0x1.5mm
L1, L2: 4.7u; NRH2410
R1, R2, R5, R6, R7, R9, R10, R11, R12, R15, R16, R17, R19, R20, R28, R29: 10K; R_0603_1608Metric
R3, R8, R13, R18: 3K3; R_0603_1608Metric
R4, R14, R26, R27, R30: 1K; R_0603_1608Metric
R21, R22: 22; R_0603_1608Metric
R23: 1K5; R_0603_1608Metric
R24: 110k; R_0603_1608Metric
R25: 100k; R_0603_1608Metric
TP1, TP2, TP3, TP4, TP5: TestPoint; TestPoint_THTPad_1.5x1.5mm_Drill0.7mm
U1: r1283; DFN-12
U2, U4: Opamp_Quad; SOIC-14
U3: DG403; TSSOP-16-1EP_4.4x5mm_P0.65mm

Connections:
+3.3V: J5.16 (3V3), R23.2, U3.12 (VL)
+5V: C3.1, J1.1 (VBUS), J5.6 (E5V), L1.1, U1.5 (CE), U1.8 (Vcc), U1.11 (PVcc)
+12V: C7.1, C10.2, C12.1, C14.1, D1.1 (K), J7.1, R24.1, R26.1, U2.4 (V+), U3.11 (V+), U4.4 (V+)
-5V: C9.1, D3.2 (A), R2.1, R9.2, R12.1, R19.2, R30.1, TP5.1
-12V: C8.2, C11.2, C13.2, C15.2, D2.2 (A), J7.2, R25.1, R27.1, R30.2, U1.4 (Voutn), U2.11 (V-), U3.14 (V-), U4.11 (V-)
/C0_FB: R2.2, R3.2, U2.9 (-), U3.5 (S4), U3.9 (S2)
/C0_IN: JP1.1 (A), JP7.2 (B), U2.5 (+)
/C0_OUT_G: R4.2, R5.2, R6.2, R7.1, TP2.1, U2.8
/C0_OUT_GO: J2.1, J3.1 (In), R10.2, U2.14
/C0_PWM_OFF: JP8.2 (B), R1.1
/C0_S_GAIN: JP5.1 (A), U3.10 (IN2)
/C0_V_OFF: R8.1, TP1.1, U2.1, U2.2 (-)
/C1_FB: R12.2, R13.2, U3.4 (S3), U3.16 (S1), U4.13 (-)
/C1_IN: JP2.1 (A), JP3.1 (A), U4.3 (+)
/C1_OUT_G: R14.2, R15.1, R16.1, R17.1, TP4.1, U4.14
/C1_OUT_GO: J2.2, J4.1 (In), R20.2, U4.8
/C1_PWM_OFF: JP6.1 (A), R11.1
/C1_S_GAIN: JP4.1 (A), U3.15 (IN1)
/C1_V_OFF: R18.1, TP3.1, U4.6 (-), U4.7
/D+: J1.3 (D+), R21.2, R23.1
/D-: J1.2 (D-), R22.2
/USB_D+: J6.12 (PA12), R21.1
/USB_D-: J6.14 (PA11), R22.1
GND: C1.2, C2.2, C3.2, C4.2, C7.2, C8.1, C9.2, C10.1, C11.1, C12.2, C13.1, C14.2, C15.1, D3.1 (K), J1.4 (GND), J1.5 (Shield), J2.3, J2.4, J3.2 (Ext), J4.2 (Ext), J5.8 (GND), J5.19 (GND), J5.20 (GND), J5.22 (GND), J6.9 (GND), J6.20 (GND), L2.2, R29.1, U1.10 (GND), U1.12 (PGND), U1.13 (GND), U2.10 (+), U2.12 (+), U3.13 (GND), U4.10 (+), U4.12 (+)
unnamed: C5.1, R26.2
unnamed: C6.1, R27.2
unnamed: D1.2 (A), L1.2, U1.2 (Lx1)
unnamed: D2.1 (K), L2.1, U1.3 (Lx2)
unnamed: J5.32 (PA4), JP7.1 (A)
unnamed: J5.38 (PC0), JP8.1 (A)
unnamed: J6.11 (PA5), JP3.2 (B)
unnamed: J6.13 (PA6), JP4.2 (B)
unnamed: J6.15 (PA7), JP5.2 (B)
unnamed: J6.17 (PB6), JP6.2 (B)
unnamed: JP1.2 (B), R3.1, U2.6 (-), U2.7
unnamed: JP2.2 (B), R13.1, U4.1, U4.2 (-)
unnamed: C5.2, R24.2, R29.2, U1.9 (Vfb1)
unnamed: C6.2, R25.2, R28.1, U1.6 (Vfb2)
unnamed: C4.1, R28.2, U1.7 (Vref)
unnamed: C1.1, R1.2, U2.3 (+)
unnamed: R6.1, R7.2, R8.2, R9.1, R10.1, U2.13 (-)
unnamed: R14.1, U3.1 (D1)
unnamed: R15.2, U3.3 (D3)
unnamed: R4.1, U3.8 (D2)
unnamed: R5.1, U3.6 (D4)
unnamed: C2.1, R11.2, U4.5 (+)
unnamed: R16.2, R17.2, R18.2, R19.1, R20.1, U4.9 (-)

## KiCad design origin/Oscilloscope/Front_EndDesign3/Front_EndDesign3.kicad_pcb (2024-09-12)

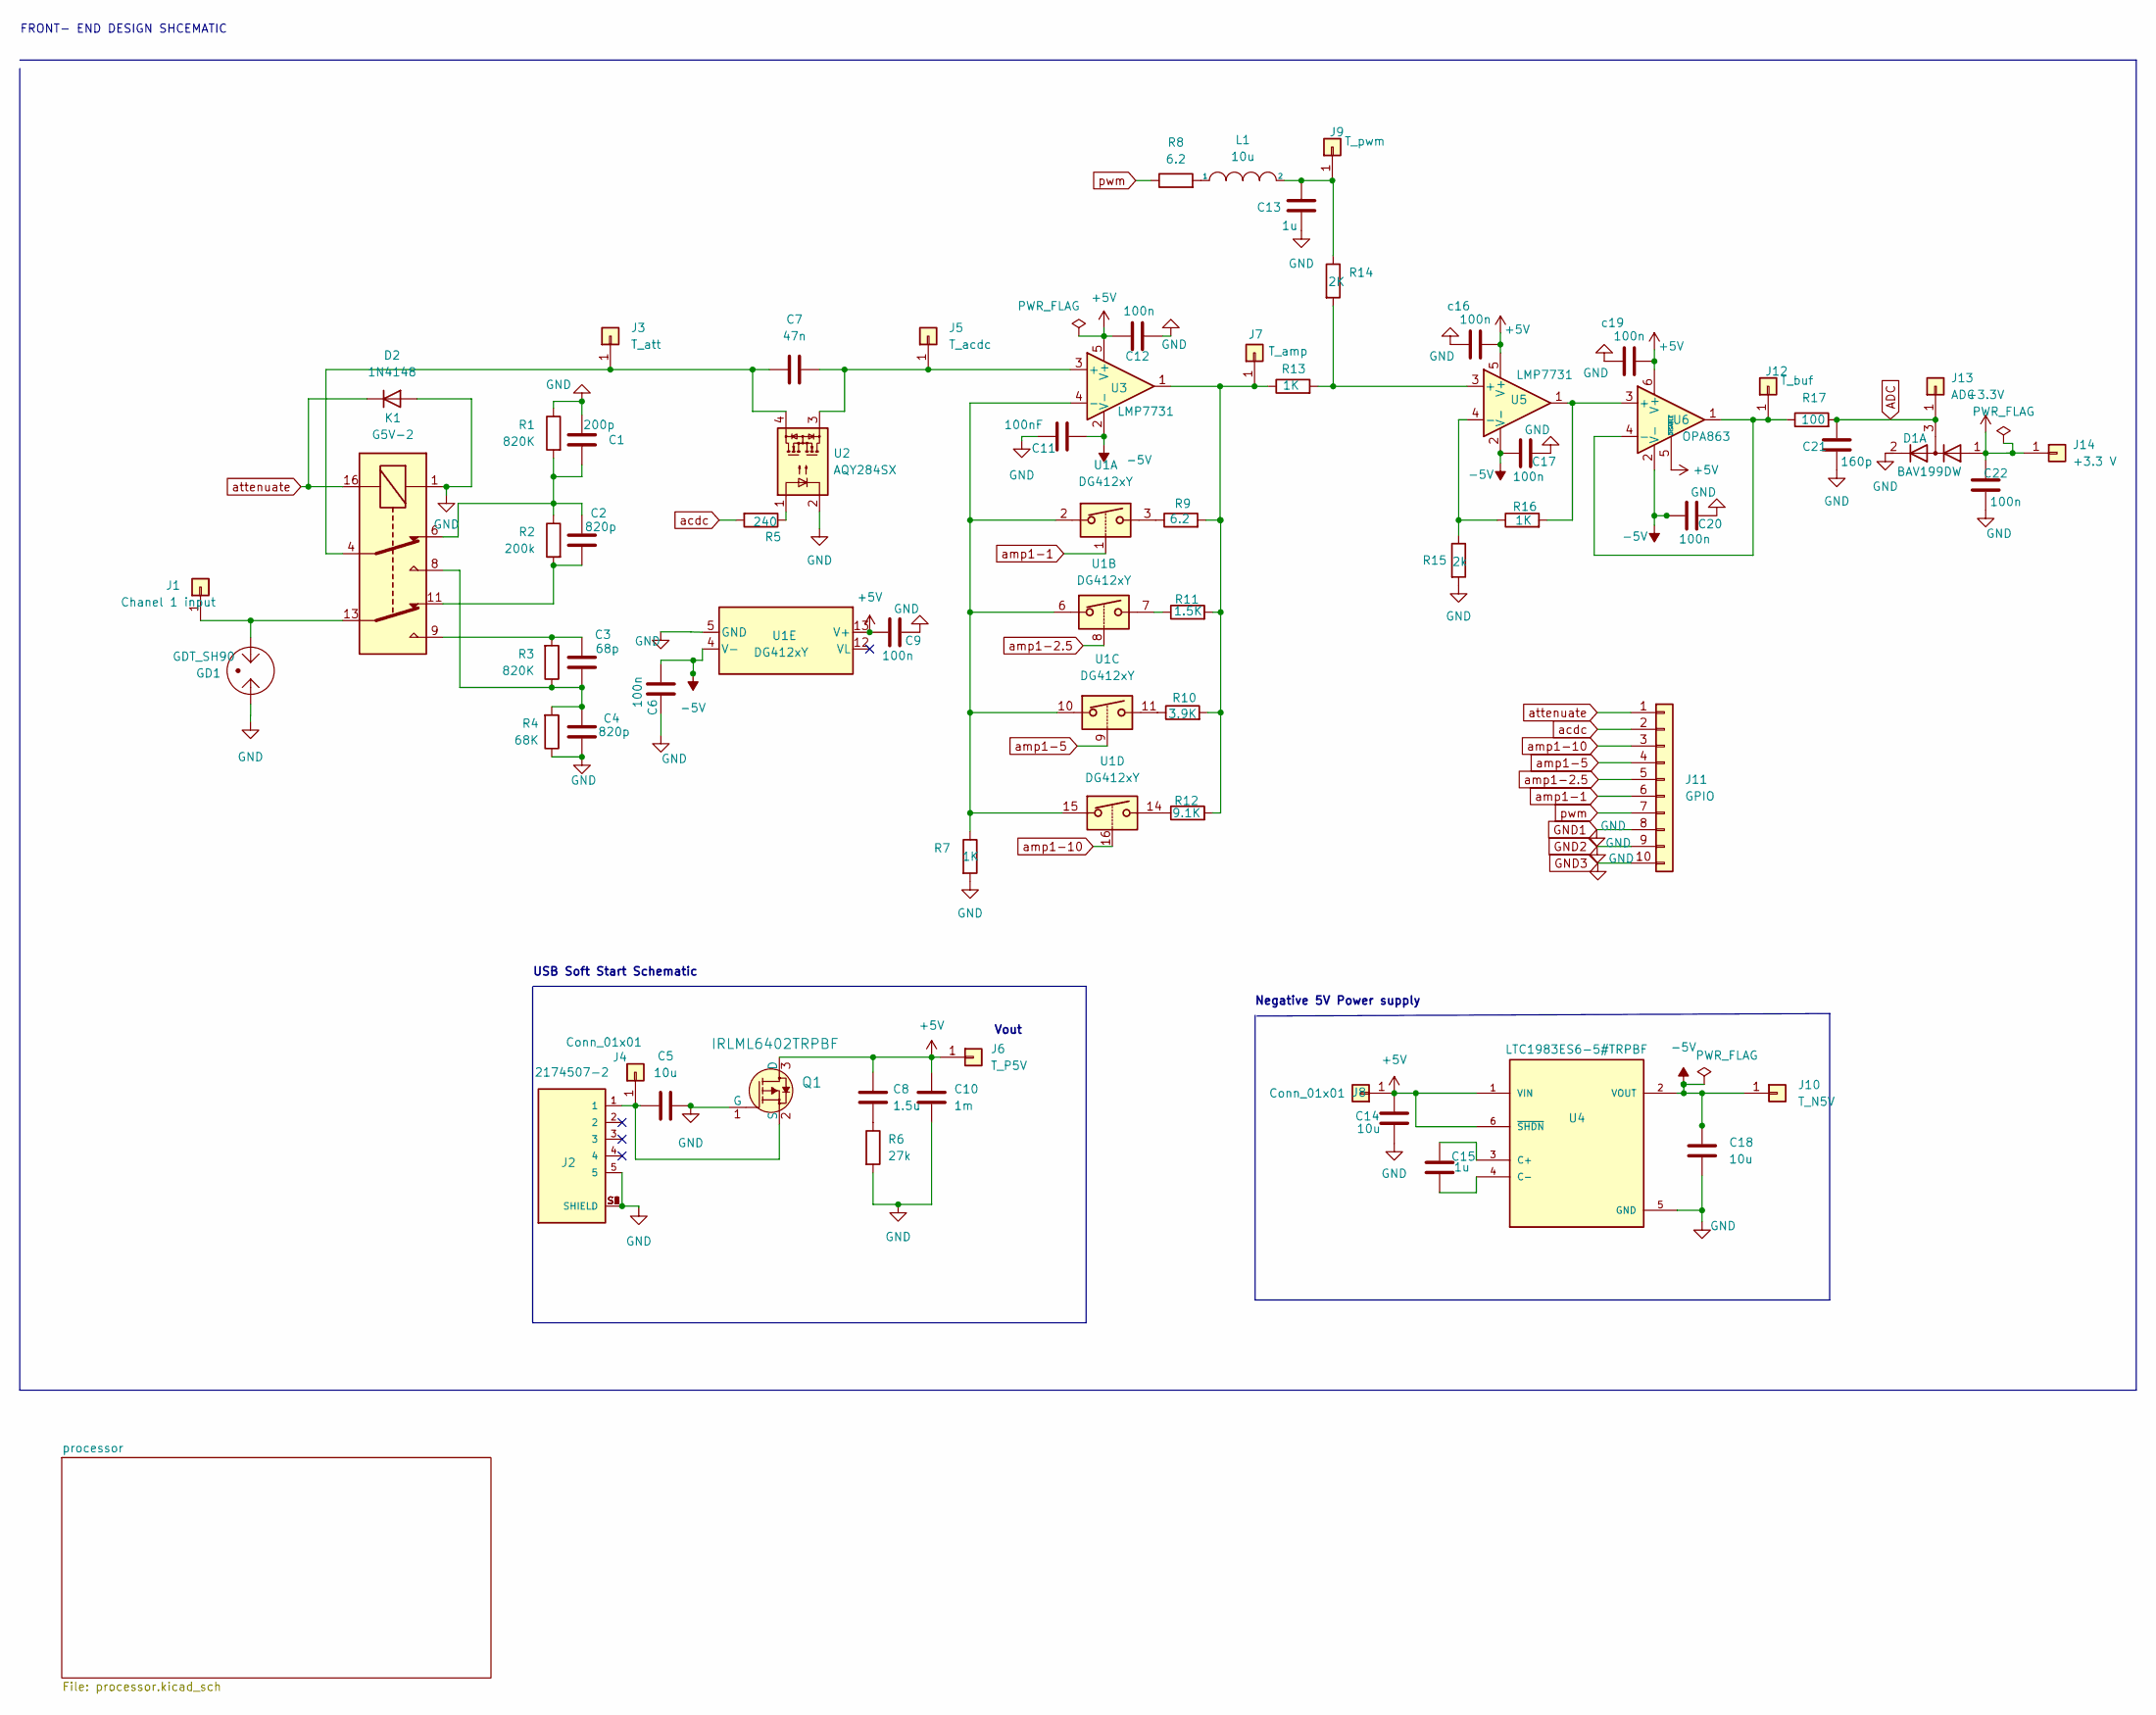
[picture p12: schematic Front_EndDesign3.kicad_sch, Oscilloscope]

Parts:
C1: 200p; C_0603_1608Metric_Pad1.08x0.95mm_HandSolder
C2, C4: 820p; C_0603_1608Metric_Pad1.08x0.95mm_HandSolder
C3: 68p; C_0603_1608Metric_Pad1.08x0.95mm_HandSolder
C5, C14, C18: 10u; C_0603_1608Metric_Pad1.08x0.95mm_HandSolder
C6, C9, C12, C17, C20, C22: 100n; C_0603_1608Metric_Pad1.08x0.95mm_HandSolder
C7: 47n; C_0603_1608Metric_Pad1.08x0.95mm_HandSolder
C8: 1.5u; C_0603_1608Metric_Pad1.08x0.95mm_HandSolder
C10: 1m; C_0603_1608Metric_Pad1.08x0.95mm_HandSolder
C11: 100nF; C_0603_1608Metric_Pad1.08x0.95mm_HandSolder
C13, C15: 1u; C_0603_1608Metric_Pad1.08x0.95mm_HandSolder
C21: 160p; C_0603_1608Metric_Pad1.08x0.95mm_HandSolder
D1: BAV199DW; SOT-23
D2: 1N4148; D_DO-35_SOD27_P7.62mm_Horizontal
GD1: GDT_SH90; SH90_1
J1: Chanel 1 input; PinHeader_1x01_P2.54mm_Vertical
J2: 2174507-2; J_SMD_2174507-2-5_7.8_5_2.71
J3: T_att; PinHeader_1x01_P2.54mm_Vertical
J4, J8: Conn_01x01; PinHeader_1x01_P2.54mm_Vertical
J5: T_acdc; PinHeader_1x01_P2.54mm_Vertical
J6: T_P5V; PinHeader_1x01_P2.54mm_Vertical
J7: T_amp; PinHeader_1x01_P2.54mm_Vertical
J9: T_pwm; PinHeader_1x01_P2.54mm_Vertical
J10: T_N5V; PinHeader_1x01_P2.54mm_Vertical
J11: GPIO; PinHeader_1x10_P2.54mm_Vertical
J12: T_buf; PinHeader_1x01_P2.54mm_Vertical
J13: ADC; PinHeader_1x01_P2.54mm_Vertical
J14: +3.3 V; PinHeader_1x01_P2.54mm_Vertical
K1: G5V-2; Relay_DPDT_Omron_G5V-2
L1: 10u; L_0603_1608Metric_Pad1.05x0.95mm_HandSolder
Q1: IRLML6402TRPBF; SOT-23-3; MPN IRLML6402TRPBF; Digi-Key_PN IRLML6402PBFCT-ND
R1, R3: 820K; R_0603_1608Metric_Pad0.98x0.95mm_HandSolder
R2: 200k; R_0603_1608Metric_Pad0.98x0.95mm_HandSolder
R4: 68K; R_0603_1608Metric_Pad0.98x0.95mm_HandSolder
R5: 240; R_0603_1608Metric_Pad0.98x0.95mm_HandSolder
R6: 27k; R_0603_1608Metric_Pad0.98x0.95mm_HandSolder
R7, R13, R16: 1K; R_0603_1608Metric_Pad0.98x0.95mm_HandSolder
R8, R9: 6.2; R_0603_1608Metric_Pad0.98x0.95mm_HandSolder
R10: 3.9K; R_0603_1608Metric_Pad0.98x0.95mm_HandSolder
R11: 1.5K; R_0603_1608Metric_Pad0.98x0.95mm_HandSolder
R12: 9.1K; R_0603_1608Metric_Pad0.98x0.95mm_HandSolder
R14: 2K; R_0603_1608Metric_Pad0.98x0.95mm_HandSolder
R15: 2k; R_0603_1608Metric_Pad0.98x0.95mm_HandSolder
R17: 100; R_0603_1608Metric_Pad0.98x0.95mm_HandSolder
U1: DG412xY; SOIC-16_3.9x9.9mm_P1.27mm
U2: AQY284SX; SOP-4_3.8x4.1mm_P2.54mm
U3, U5: LMP7731; SOT-23-5_HandSoldering
U4: LTC1983ES6-5#TRPBF; SOT-23-6_Handsoldering; PARTREV C
U6: OPA863; SOT-23-6_Handsoldering
c16, c19: 100n; C_0603_1608Metric_Pad1.08x0.95mm_HandSolder

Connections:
+3.3V: C22.1, D1.1 (A1), J14.1
+5V: C8.2, C9.1, C10.1, C12.1, C14.1, J6.1, J8.1, Q1.3 (D), U1.13 (V+), U3.5 (V+), U4.1 (VIN), U4.6 (~SHDN), U5.5 (V+), U6.5 (~DISABLE), U6.6 (V+), c16.2, c19.2
-5V: C6.1, C11.2, C17.1, C18.1, C20.1, J10.1, U1.4 (V-), U3.2 (V-), U4.2 (VOUT), U5.2 (V-), U6.2 (V-)
GND: C1.1, C4.2, C5.2, C6.2, C9.2, C10.2, C11.1, C12.2, C13.2, C14.2, C17.2, C18.2, C20.2, C21.2, C22.2, D1.2 (K2), D2.2 (A), GD1.2, J2.5, J2.S1 (SHIELD), J2.S2 (SHIELD), J2.S3 (SHIELD), J2.S4 (SHIELD), J2.S5 (SHIELD), J2.S6 (SHIELD), J11.8, J11.9, J11.10, K1.1, Q1.1 (G), R1.1, R4.1, R6.2, R7.2, R15.2, U1.5 (GND), U2.2, U4.5 (GND), c16.1, c19.1
unnamed: C1.2, C2.1, K1.6, R1.2, R2.1
unnamed: C2.2, K1.11, R2.2
unnamed: C3.1, K1.9, R3.2
unnamed: C3.2, C4.1, K1.8, R3.1, R4.2
unnamed: C5.1, J2.1, J4.1, Q1.2 (S)
unnamed: C7.1, J3.1, K1.4, U2.4
unnamed: C7.2, J5.1, U2.3, U3.3 (+)
unnamed: C8.1, R6.1
unnamed: C13.1, J9.1, L1.2, R14.1
unnamed: C15.1, U4.3 (C+)
unnamed: C15.2, U4.4 (C-)
unnamed: C21.1, D1.3 (K3A4), J13.1, R17.2
unnamed: GD1.1, J1.1, K1.13
unnamed: J7.1, R9.2, R10.2, R11.2, R12.2, R13.1, U3.1
unnamed: J12.1, R17.1, U6.1, U6.4 (-)
unnamed: L1.1, R8.2
unnamed: R5.1, U2.1
unnamed: R7.1, U1.2, U1.6, U1.10, U1.15, U3.4 (-)
unnamed: R9.1, U1.3
unnamed: R10.1, U1.11
unnamed: R11.1, U1.7
unnamed: R12.1, U1.14
unnamed: R13.2, R14.2, U5.3 (+)
unnamed: R15.1, R16.1, U5.4 (-)
unnamed: R16.2, U5.1, U6.3 (+)
acdc: J11.2, R5.2
amp1-1: J11.6, U1.1
amp1-2.5: J11.5, U1.8
amp1-5: J11.4, U1.9
amp1-10: J11.3, U1.16
attenuate: D2.1 (K), J11.1, K1.16
pwm: J11.7, R8.1

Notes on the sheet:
Vout
USB Soft Start Schematic
Negative 5V Power supply
FRONT- END DESIGN SHCEMATIC

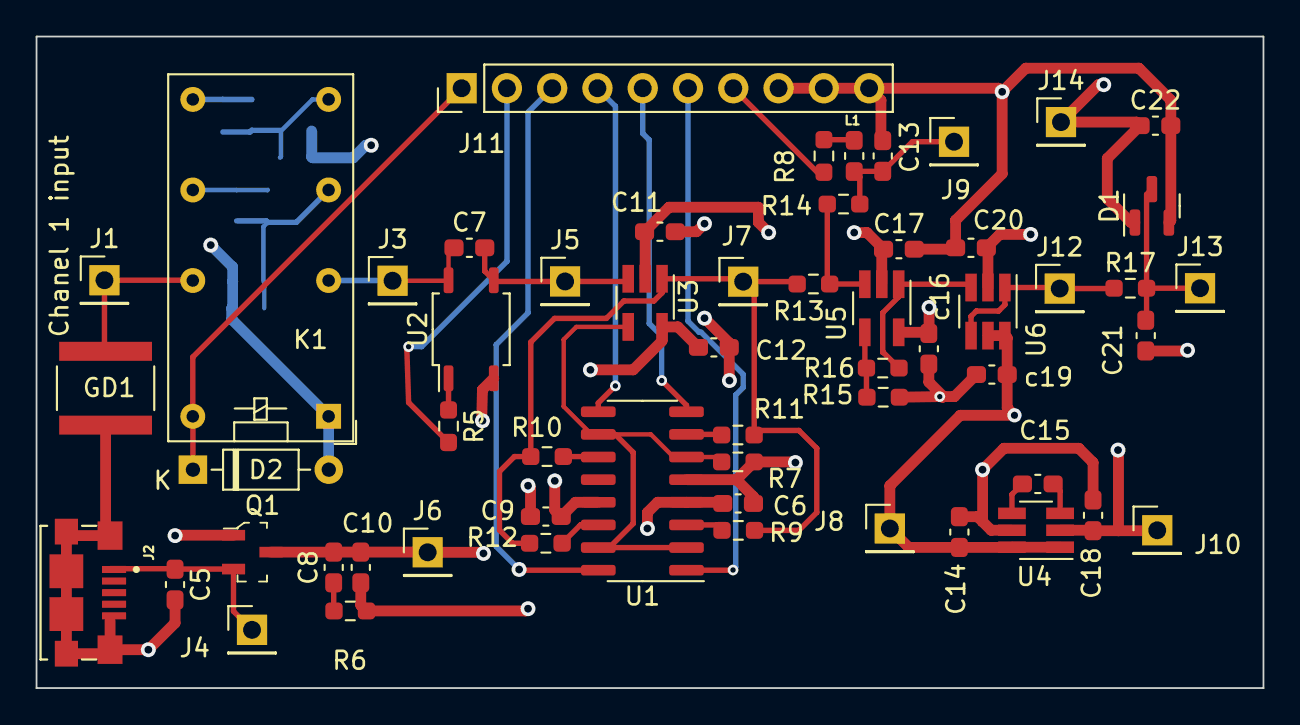
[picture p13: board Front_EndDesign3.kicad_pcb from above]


Board: 4 copper layers, 68.8 x 36.6 mm, 65 parts (8 on the bottom side), 36 nets.

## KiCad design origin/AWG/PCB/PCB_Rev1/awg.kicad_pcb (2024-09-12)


Board: 2 copper layers, 44.7 x 42.9 mm, 62 parts (0 on the bottom side), 37 nets.

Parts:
C1, C2, C3, C5, C7: 10u; C_0805_2012Metric_Pad1.18x1.45mm_HandSolder
C4, C6: 120p; C_0603_1608Metric_Pad1.08x0.95mm_HandSolder
C8, C9, C10, C11, C12, C13, C14, C15, C16: 100n; C_0603_1608Metric_Pad1.08x0.95mm_HandSolder
D1, D2: S14
D3: LM4040-5; SOT-23
J1: 02x05; 2x05
J2: 02x02; 2x02
J3, J4: 01x02; PinHeader_1x02_P2.54mm_Vertical
L1, L2: 4.7u; NRH2410
R1, R3, R4, R6, R7, R8, R10, R11, R13, R14, R18, R20, R23, R26: 10K; R_0603_1608Metric
R2, R5, R9, R12: 3K3; R_0603_1608Metric
R15, R16, R17, R19, R22, R25, R27: 1K; R_0603_1608Metric
R21: 110k; R_0603_1608Metric
R24: 100k; R_0603_1608Metric
TP1, TP2, TP3, TP4, TP5: TestPoint; TestPoint_THTPad_2.0x2.0mm_Drill1.0mm
U1, U2, U3: LM2904; SOT-23-8_Handsoldering
U4: DG403; TSSOP-16-1EP_4.4x5mm_P0.65mm
U5: r1283; DFN-12

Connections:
+3.3V: J1.3, U4.12 (VL)
+5V: C3.1, J1.4, L1.1, U5.5 (CE), U5.8 (Vcc), U5.11 (PVcc)
+12V: C9.2, C11.1, C13.1, C15.1, J3.1, U1.8 (V+), U2.8 (V+), U3.8 (V+), U4.11 (V+)
-5V: D3.2 (A), R1.1, R6.2, R8.1, R13.2, R27.1, TP5.1
-12V: C10.2, C12.2, C14.2, C16.2, J4.2, R27.2, U1.4 (V-), U2.4 (V-), U3.4 (V-), U4.14 (V-)
/C0_FB: R1.2, R2.2, U1.2 (-), U4.4 (S3), U4.16 (S1)
/C0_IN: J1.9, R2.1
/C0_OUT_G: R3.2, R4.1, R17.2, R18.1, TP1.1, U1.1
/C0_OUT_GO: J2.2, R7.2, U1.7
/C0_PWM_OFF: J1.1, R15.1
/C0_S_GAIN: J1.7, U4.15 (IN1)
/C0_V_OFF: R5.1, TP3.1, U3.1, U3.2 (-)
/C1_FB: R8.2, R9.2, U2.2 (-), U4.5 (S4), U4.9 (S2)
/C1_IN: J1.8, R9.1
/C1_OUT_G: R10.1, R11.1, R19.2, R20.2, TP2.1, U2.1
/C1_OUT_GO: J2.1, R14.2, U2.7
/C1_PWM_OFF: J1.2, R16.1
/C1_S_GAIN: J1.6, U4.10 (IN2)
/C1_V_OFF: R12.1, TP4.1, U3.6 (-), U3.7
GND: C1.2, C2.2, C3.2, C5.2, C7.1, C8.2, C9.1, C10.1, C11.2, C12.1, C13.2, C14.1, C15.2, C16.1, D3.1 (K), J1.5, J1.10, J2.3, J2.4, L2.2, R23.1, U1.3 (+), U1.5 (+), U2.3 (+), U2.5 (+), U4.13 (GND), U5.10 (GND), U5.12 (PGND), U5.13 (GND)
unnamed: C4.1, R22.2
unnamed: C6.1, R25.2
unnamed: D1.2 (A), L1.2, U5.2 (Lx1)
unnamed: C5.1, D1.1 (K), J3.2, R21.1, R22.1
unnamed: C7.2, D2.2 (A), J4.1, R24.1, R25.1, U5.4 (Voutn)
unnamed: D2.1 (K), L2.1, U5.3 (Lx2)
unnamed: R3.1, R4.2, R5.2, R6.1, R7.1, U1.6 (-)
unnamed: R10.2, R11.2, R12.2, R13.1, R14.1, U2.6 (-)
unnamed: C1.1, R15.2, U3.3 (+)
unnamed: C2.1, R16.2, U3.5 (+)
unnamed: R17.1, U4.1 (D1)
unnamed: R19.1, U4.8 (D2)
unnamed: R18.2, U4.3 (D3)
unnamed: R20.1, U4.6 (D4)
unnamed: C4.2, R21.2, R23.2, U5.9 (Vfb1)
unnamed: C6.2, R24.2, R26.1, U5.6 (Vfb2)
unnamed: C8.1, R26.2, U5.7 (Vref)

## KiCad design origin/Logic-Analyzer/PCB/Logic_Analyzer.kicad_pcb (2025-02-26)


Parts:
C1, C2, C4, C5: 100nF; C_0603_1608Metric
C3: 1uF; C_0603_1608Metric
D2: LED; LED_0603_1608Metric
J1: USB Micro; USB_Micro-B_Amphenol_10118194_Horizontal
J2: nuc303_LEFT; PinSocket_2x19_P2.54mm_Vertical
J3: 30320-5002HB; 303205002HB; Mouser Part Number 517-30320-5002
J5: nuc303_RIGHT; PinSocket_2x19_P2.54mm_Vertical
Q2: PMOS; TO-263-2
R1, R6, R7, R8, R9, R10, R11, R12, R13, R14, R15, R16, R17, R18, R19, R20, R21: 1M; R_0603_1608Metric
R2, R4: 22; R_0603_1608Metric
R3: 1k; R_0603_1608Metric
R5: 1.5k; R_0603_1608Metric
U1, U3: 74HC245N; SOIC-20W_7.5x12.8mm_P1.27mm; PARTREV 03

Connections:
+3V3: C4.1, C5.2, J2.16 (3V3), R5.2, U1.20 (VCC), U3.20 (VCC)
+5V: C2.1, J2.6 (E5V), Q2.2 (G), R3.1
/D+: J1.3 (D+), R2.2, R5.1
/D-: J1.2 (D-), R4.1
/PB0: J2.34 (PB0), U1.2 (A0)
/PB1: J5.24 (PB1), U3.2 (A0)
/PB2: J5.22 (PB2), U3.3 (A1)
/PB3: J5.31 (PB3), U1.3 (A1)
/PB4: J5.27 (PB4), U1.6 (A4)
/PB5: J5.29 (PB5), U1.4 (A2)
/PB6: J5.17 (PB6), U3.4 (A2)
/PB7: J2.21 (PB7), U3.9 (A7)
/PB8: J5.3 (PB8), U3.8 (A6)
/PB9: J5.5 (PB9), U3.7 (A5)
/PB10: J5.25 (PB10), U1.8 (A6)
/PB11: J5.18 (PB11), U3.5 (A3)
/PB12: J5.16 (PB12), U3.6 (A4)
/PB13: J5.30 (PB13), U1.5 (A3)
/PB14: J5.28 (PB14), U1.7 (A5)
/PB15: J5.26 (PB15), U1.9 (A7)
/VBUS: C1.1, C3.1, J1.1 (VBUS), Q2.3 (S)
GND: C3.2, C4.2, C5.1, D2.1 (K), J1.4 (GND), J1.5 (Shield), J2.8 (GND), J2.19 (GND), J2.20 (GND), J2.22 (GND), J3.1, J3.2, J3.19, J3.20, J5.9 (GND), J5.20 (GND), R1.2, R6.1, R7.2, R8.1, R9.2, R10.1, R11.2, R12.2, R13.1, R14.2, R15.2, R16.2, R17.2, R18.1, R19.1, R20.1, R21.1, U1.1 (DIR), U1.10 (GND), U1.19 (~OE), U3.1 (DIR), U3.10 (GND), U3.19 (~OE)
unnamed: D2.2 (A), R3.2
unnamed: J5.14 (PA11), R4.2
unnamed: J5.12 (PA12), R2.1
unnamed: C1.2, C2.2, Q2.1 (D), R1.1
unnamed: J3.3, R14.1, U1.18 (B0)
unnamed: J3.4, R18.2, U1.17 (B1)
unnamed: J3.5, R15.1, U1.16 (B2)
unnamed: J3.6, R19.2, U1.15 (B3)
unnamed: J3.7, R16.1, U1.14 (B4)
unnamed: J3.8, R21.2, U1.13 (B5)
unnamed: J3.9, R17.1, U1.12 (B6)
unnamed: J3.10, R20.2, U1.11 (B7)
unnamed: J3.11, R12.1, U3.18 (B0)
unnamed: J3.12, R8.2, U3.17 (B1)
unnamed: J3.13, R9.1, U3.16 (B2)
unnamed: J3.14, R13.2, U3.15 (B3)
unnamed: J3.15, R11.1, U3.14 (B4)
unnamed: J3.16, R10.2, U3.13 (B5)
unnamed: J3.17, R7.1, U3.12 (B6)
unnamed: J3.18, R6.2, U3.11 (B7)

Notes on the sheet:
USB Softstart
Nucleo Board + USB
Bus Tranceivers


Board: 2 copper layers, 70.1 x 64.7 mm, 34 parts (0 on the bottom side), 42 nets.

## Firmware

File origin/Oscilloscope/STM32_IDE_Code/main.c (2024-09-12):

/* USER CODE BEGIN Header */
/**
  ******************************************************************************
  * @file           : main.c
  * @brief          : Main program body
  ******************************************************************************
  * @attention
  *
  * Copyright (c) 2022 STMicroelectronics.
  * All rights reserved.
  *
  * This software is licensed under terms that can be found in the LICENSE file
  * in the root directory of this software component.
  * If no LICENSE file comes with this software, it is provided AS-IS.
  *
  ******************************************************************************
  */
/* USER CODE END Header */
/* Includes ------------------------------------------------------------------*/
#include "main.h"
#include "usb_device.h"

/* Private includes ----------------------------------------------------------*/
/* USER CODE BEGIN Includes */
#include "usbd_cdc_if.h"
#include <string.h>
#include <stdio.h>
#include <stdlib.h>
#include <math.h>
#include <stm32f3xx_ll_adc.h>
#include <stm32f3xx_ll_rcc.h>
/* USER CODE END Includes */

/* Private typedef -----------------------------------------------------------*/
/* USER CODE BEGIN PTD */

/* USER CODE END PTD */

/* Private define ------------------------------------------------------------*/
/* USER CODE BEGIN PD */
#define ADC_BUFF 10000	// can be 20480 make larger buffer => store more data
void changeSampling(ADC_HandleTypeDef* hadc);	// declare function before using it
/* USER CODE END PD */

/* Private macro -------------------------------------------------------------*/
/* USER CODE BEGIN PM */

/* USER CODE END PM */

/* Private variables ---------------------------------------------------------*/
ADC_HandleTypeDef hadc1;
DMA_HandleTypeDef hdma_adc1;

TIM_HandleTypeDef htim1;
TIM_HandleTypeDef htim16;
DMA_HandleTypeDef hdma_tim1_ch1;

UART_HandleTypeDef huart2;

/* USER CODE BEGIN PV */
uint8_t command_buffer[64];
uint16_t adc_buff[ADC_BUFF];
char offset[5];
char digit1;
char digit2;
char digit3;
char digit4;
int ccr_digit1234=0;
/* USER CODE END PV */

/* Private function prototypes -----------------------------------------------*/
void SystemClock_Config(void);
static void MX_GPIO_Init(void);
static void MX_DMA_Init(void);
static void MX_ADC1_Init(void);
static void MX_TIM16_Init(void);
static void MX_TIM1_Init(void);
static void MX_USART2_UART_Init(void);
/* USER CODE BEGIN PFP */
void changeADC1Clock1();
void changeADC1Clock2();
void changeADC1Clock4();
void changeADC1Clock6();
void changeADC1Clock8();
void changeADC1Clock10();
void changeADC1Clock12();
void changeADC1Clock16();
void changeADC1Clock32();
void changeADC1Clock64();
void changeADC1Clock128();
void changeADC1Clock256();

void changeSampling0(ADC_HandleTypeDef* hadc);	// declare function before using it
void changeSampling1(ADC_HandleTypeDef* hadc);
void changeSampling2(ADC_HandleTypeDef* hadc);
void changeSampling3(ADC_HandleTypeDef* hadc);
void changeSampling4(ADC_HandleTypeDef* hadc);
void changeSampling5(ADC_HandleTypeDef* hadc);
void changeSampling6(ADC_HandleTypeDef* hadc);
void changeSampling7(ADC_HandleTypeDef* hadc);
/* USER CODE END PFP */

/* Private user code ---------------------------------------------------------*/
/* USER CODE BEGIN 0 */

/* USER CODE END 0 */

/**
  * @brief  The application entry point.
  * @retval int
  */
int main(void)
{
  /* USER CODE BEGIN 1 */
	char msg[10];
	int n=0;
	int a=0;
  /* USER CODE END 1 */

  /* MCU Configuration--------------------------------------------------------*/

  /* Reset of all peripherals, Initializes the Flash interface and the Systick. */
  HAL_Init();

  /* USER CODE BEGIN Init */

  /* USER CODE END Init */

  /* Configure the system clock */
  SystemClock_Config();

  /* USER CODE BEGIN SysInit */

  /* USER CODE END SysInit */

  /* Initialize all configured peripherals */
  MX_GPIO_Init();
  MX_DMA_Init();
  MX_ADC1_Init();
  MX_TIM16_Init();
  MX_USB_DEVICE_Init();
  MX_TIM1_Init();
  MX_USART2_UART_Init();
  /* USER CODE BEGIN 2 */
  HAL_ADC_Start_DMA(&hadc1, (uint32_t*)adc_buff, ADC_BUFF);
  HAL_TIM_PWM_Start(&htim1, TIM_CHANNEL_1);
  TIM1->CCR1 = 3300;
  /* USER CODE END 2 */

  /* Infinite loop */
  /* USER CODE BEGIN WHILE */
  while (1)
    {

	  //-------------------Original------------------------------------
	  //TIM1->CCR1 = ccr_digit1234;
	  if (n==10000){
  		  n=0;
  	  }
  	  // copy adc (16 bits) value from buffer to (char) msg
  	  // this sprintf() COPY adc_buff valaue,
  	  // CONVERT to "short unsigned" by %hu, PASTE to msg
  	  sprintf(msg, "%hu\r\n", adc_buff[n]);
  	  CDC_Transmit_FS((uint8_t *)msg, strlen(msg));
  	  HAL_Delay(1);
  	  n++;
  	  if (command_buffer[0]=='1'){				// command string is new?
		  digit1 = command_buffer[4];
		  digit2 = command_buffer[5];
		  digit3 = command_buffer[6];
		  digit4 = command_buffer[7];
		  sprintf(offset, "%c%c%c%c",digit1, digit2, digit3, digit4);
		  sscanf(offset, "%04d", &ccr_digit1234);
		  //--------------------Set ADC Clock-----------------------
		  if (command_buffer[3]=='0' && command_buffer[2]=='0'){
			  changeADC1Clock1();
		  }
		  else if(command_buffer[3]=='1' && command_buffer[2]=='0'){
			  changeADC1Clock2();
		  }
		  else if(command_buffer[3]=='2' && command_buffer[2]=='0'){
			  changeADC1Clock4();
		  }
		  else if(command_buffer[3]=='3' && command_buffer[2]=='0'){
			  changeADC1Clock6();
		  }
		  else if(command_buffer[3]=='4' && command_buffer[2]=='0'){
			  changeADC1Clock8();
		  }
		  else if(command_buffer[3]=='5' && command_buffer[2]=='0'){
			  changeADC1Clock10();
		  }
		  else if(command_buffer[3]=='6' && command_buffer[2]=='0'){
			  changeADC1Clock12();
		  }
		  else if(command_buffer[3]=='7' && command_buffer[2]=='0'){
			  changeADC1Clock16();
		  }
		  else if(command_buffer[3]=='8' && command_buffer[2]=='0'){
			  changeADC1Clock32();
		  }
		  else if(command_buffer[3]=='9' && command_buffer[2]=='0'){
			  changeADC1Clock64();
		  }
		  else if(command_buffer[2]=='1' && command_buffer[3]=='0'){
			  changeADC1Clock128();
		  }
		  else if(command_buffer[2]=='1' && command_buffer[3]=='1'){
			  changeADC1Clock256();
		  }

		  //--------------------Set Sample Time-----------------------
		  if (command_buffer[1]=='0'){			// SMP 1.5 clock cycles
			  changeSampling0(&hadc1);
		  }
		  else if (command_buffer[1]=='1'){	// SMP 2.5 clock cycles
			  changeSampling1(&hadc1);
		  }
		  else if (command_buffer[1]=='2'){	// SMP 4.5 clock cycles
			  changeSampling2(&hadc1);
		  }
		  else if (command_buffer[1]=='3'){	// SMP 7.5 clock cycles
			  changeSampling3(&hadc1);
		  }
		  else if (command_buffer[1]=='4'){	// SMP 19.5 clock cycles
			  changeSampling4(&hadc1);
		  }
		  else if (command_buffer[1]=='5'){	// SMP 61.5 clock cycles
			  changeSampling5(&hadc1);
		  }
		  else if (command_buffer[1]=='6'){	// SMP 181.5 clock cycles
			  changeSampling6(&hadc1);
		  }
		  else if (command_buffer[1]=='7'){	// SMP 601.5 clock cycles
			  changeSampling7(&hadc1);
		  }
		  if (command_buffer[8]=='1'){
			  HAL_GPIO_WritePin(GPIOA, GPIO_PIN_10, SET);
		  }
		  else{
			  HAL_GPIO_WritePin(GPIOA, GPIO_PIN_10, RESET);
		  }
		  if (command_buffer[9]=='1'){
			  HAL_GPIO_WritePin(GPIOA, GPIO_PIN_9, SET);
		  }
		  else{
			  HAL_GPIO_WritePin(GPIOA, GPIO_PIN_9, RESET);
		  }
		  if (command_buffer[10]=='1'){
			  HAL_GPIO_WritePin(GPIOA, GPIO_PIN_8, SET);
		  }
		  else{
			  HAL_GPIO_WritePin(GPIOA, GPIO_PIN_8, RESET);
		  }
		  if (command_buffer[11]=='1'){
			  HAL_GPIO_WritePin(GPIOC, GPIO_PIN_7, SET);
		  }
		  else{
			  HAL_GPIO_WritePin(GPIOC, GPIO_PIN_7, RESET);
		  }
		  if (command_buffer[12]=='1'){
			  HAL_GPIO_WritePin(GPIOB, GPIO_PIN_10, SET);
		  }
		  else{
			  HAL_GPIO_WritePin(GPIOB, GPIO_PIN_10, RESET);
		  }
		  if (command_buffer[13]=='1'){
			  HAL_GPIO_WritePin(GPIOB, GPIO_PIN_4, SET);
		  }
		  else{
			  HAL_GPIO_WritePin(GPIOB, GPIO_PIN_4, RESET);
		  }
		  command_buffer[0]='0';		// set this command string becomes old
	  }
    /* USER CODE END WHILE */

    /* USER CODE BEGIN 3 */
    }
  /* USER CODE END 3 */
}

/**
  * @brief System Clock Configuration
  * @retval None
  */
void SystemClock_Config(void)
{
  RCC_OscInitTypeDef RCC_OscInitStruct = {0};
  RCC_ClkInitTypeDef RCC_ClkInitStruct = {0};
  RCC_PeriphCLKInitTypeDef PeriphClkInit = {0};

  /** Initializes the RCC Oscillators according to the specified parameters
  * in the RCC_OscInitTypeDef structure.
  */
  RCC_OscInitStruct.OscillatorType = RCC_OSCILLATORTYPE_HSE;
  RCC_OscInitStruct.HSEState = RCC_HSE_ON;
  RCC_OscInitStruct.HSIState = RCC_HSI_ON;
  RCC_OscInitStruct.PLL.PLLState = RCC_PLL_ON;
  RCC_OscInitStruct.PLL.PLLSource = RCC_PLLSOURCE_HSE;
  RCC_OscInitStruct.PLL.PLLMUL = RCC_PLL_MUL9;
  RCC_OscInitStruct.PLL.PREDIV = RCC_PREDIV_DIV1;
  if (HAL_RCC_OscConfig(&RCC_OscInitStruct) != HAL_OK)
  {
    Error_Handler();
  }

  /** Initializes the CPU, AHB and APB buses clocks
  */
  RCC_ClkInitStruct.ClockType = RCC_CLOCKTYPE_HCLK|RCC_CLOCKTYPE_SYSCLK
                              |RCC_CLOCKTYPE_PCLK1|RCC_CLOCKTYPE_PCLK2;
  RCC_ClkInitStruct.SYSCLKSource = RCC_SYSCLKSOURCE_PLLCLK;
  RCC_ClkInitStruct.AHBCLKDivider = RCC_SYSCLK_DIV1;
  RCC_ClkInitStruct.APB1CLKDivider = RCC_HCLK_DIV2;
  RCC_ClkInitStruct.APB2CLKDivider = RCC_HCLK_DIV1;

  if (HAL_RCC_ClockConfig(&RCC_ClkInitStruct, FLASH_LATENCY_2) != HAL_OK)
  {
    Error_Handler();
  }
  PeriphClkInit.PeriphClockSelection = RCC_PERIPHCLK_USB|RCC_PERIPHCLK_USART2
                              |RCC_PERIPHCLK_TIM1|RCC_PERIPHCLK_TIM16
                              |RCC_PERIPHCLK_ADC12;
  PeriphClkInit.Usart2ClockSelection = RCC_USART2CLKSOURCE_PCLK1;
  PeriphClkInit.Adc12ClockSelection = RCC_ADC12PLLCLK_DIV1;
  PeriphClkInit.USBClockSelection = RCC_USBCLKSOURCE_PLL_DIV1_5;
  PeriphClkInit.Tim1ClockSelection = RCC_TIM1CLK_HCLK;
  PeriphClkInit.Tim16ClockSelection = RCC_TIM16CLK_HCLK;
  if (HAL_RCCEx_PeriphCLKConfig(&PeriphClkInit) != HAL_OK)
  {
    Error_Handler();
  }
}

/**
  * @brief ADC1 Initialization Function
  * @param None
  * @retval None
  */
static void MX_ADC1_Init(void)
{

  /* USER CODE BEGIN ADC1_Init 0 */

  /* USER CODE END ADC1_Init 0 */

  ADC_MultiModeTypeDef multimode = {0};
  ADC_ChannelConfTypeDef sConfig = {0};

  /* USER CODE BEGIN ADC1_Init 1 */

  /* USER CODE END ADC1_Init 1 */

  /** Common config
  */
  hadc1.Instance = ADC1;
  hadc1.Init.ClockPrescaler = ADC_CLOCK_ASYNC_DIV1;
  hadc1.Init.Resolution = ADC_RESOLUTION_12B;
  hadc1.Init.ScanConvMode = ADC_SCAN_DISABLE;
  hadc1.Init.ContinuousConvMode = ENABLE;
  hadc1.Init.DiscontinuousConvMode = DISABLE;
  hadc1.Init.ExternalTrigConvEdge = ADC_EXTERNALTRIGCONVEDGE_NONE;
  hadc1.Init.ExternalTrigConv = ADC_SOFTWARE_START;
  hadc1.Init.DataAlign = ADC_DATAALIGN_RIGHT;
  hadc1.Init.NbrOfConversion = 1;
  hadc1.Init.DMAContinuousRequests = ENABLE;
  hadc1.Init.EOCSelection = ADC_EOC_SINGLE_CONV;
  hadc1.Init.LowPowerAutoWait = DISABLE;
  hadc1.Init.Overrun = ADC_OVR_DATA_OVERWRITTEN;
  if (HAL_ADC_Init(&hadc1) != HAL_OK)
  {
    Error_Handler();
  }

  /** Configure the ADC multi-mode
  */
  multimode.Mode = ADC_MODE_INDEPENDENT;
  if (HAL_ADCEx_MultiModeConfigChannel(&hadc1, &multimode) != HAL_OK)
  {
    Error_Handler();
  }

  /** Configure Regular Channel
  */
  sConfig.Channel = ADC_CHANNEL_1;
  sConfig.Rank = ADC_REGULAR_RANK_1;
  sConfig.SingleDiff = ADC_SINGLE_ENDED;
  sConfig.SamplingTime = ADC_SAMPLETIME_1CYCLE_5;
  sConfig.OffsetNumber = ADC_OFFSET_NONE;
  sConfig.Offset = 0;
  if (HAL_ADC_ConfigChannel(&hadc1, &sConfig) != HAL_OK)
  {
    Error_Handler();
  }
  /* USER CODE BEGIN ADC1_Init 2 */

  /* USER CODE END ADC1_Init 2 */

}
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

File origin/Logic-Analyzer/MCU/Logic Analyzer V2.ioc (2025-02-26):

#MicroXplorer Configuration settings - do not modify
CAD.formats=
CAD.pinconfig=
CAD.provider=
File.Version=6
KeepUserPlacement=false
Mcu.CPN=STM32F303RET6
Mcu.Family=STM32F3
Mcu.IP0=NVIC
Mcu.IP1=RCC
Mcu.IP2=SYS
Mcu.IP3=TIM2
Mcu.IP4=TIM16
Mcu.IP5=USB
Mcu.IP6=USB_DEVICE
Mcu.IPNb=7
Mcu.Name=STM32F303R(D-E)Tx
Mcu.Package=LQFP64
Mcu.Pin0=PC13
Mcu.Pin1=PC14-OSC32_IN
Mcu.Pin10=PB11
Mcu.Pin11=PB12
Mcu.Pin12=PB13
Mcu.Pin13=PB14
Mcu.Pin14=PB15
Mcu.Pin15=PA11
Mcu.Pin16=PA12
Mcu.Pin17=PA13
Mcu.Pin18=PA14
Mcu.Pin19=PB3
Mcu.Pin2=PC15-OSC32_OUT
Mcu.Pin20=PB4
Mcu.Pin21=PB5
Mcu.Pin22=PB6
Mcu.Pin23=PB7
Mcu.Pin24=PB8
Mcu.Pin25=PB9
Mcu.Pin26=VP_SYS_VS_Systick
Mcu.Pin27=VP_TIM2_VS_no_output1
Mcu.Pin28=VP_TIM2_VS_no_output2
Mcu.Pin29=VP_TIM16_VS_ClockSourceINT
Mcu.Pin3=PF0-OSC_IN
Mcu.Pin30=VP_USB_DEVICE_VS_USB_DEVICE_CDC_FS
Mcu.Pin4=PF1-OSC_OUT
Mcu.Pin5=PA5
Mcu.Pin6=PB0
Mcu.Pin7=PB1
Mcu.Pin8=PB2
Mcu.Pin9=PB10
Mcu.PinsNb=31
Mcu.ThirdPartyNb=0
Mcu.UserConstants=
Mcu.UserName=STM32F303RETx
MxCube.Version=6.10.0
MxDb.Version=DB.6.0.100
NVIC.BusFault_IRQn=true\:0\:0\:false\:false\:true\:true\:false\:false
NVIC.DebugMonitor_IRQn=true\:0\:0\:false\:false\:true\:true\:false\:false
NVIC.ForceEnableDMAVector=true
NVIC.HardFault_IRQn=true\:0\:0\:false\:false\:true\:true\:false\:false
NVIC.MemoryManagement_IRQn=true\:0\:0\:false\:false\:true\:true\:false\:false
NVIC.NonMaskableInt_IRQn=true\:0\:0\:false\:false\:true\:true\:false\:false
NVIC.PendSV_IRQn=true\:0\:0\:false\:false\:true\:false\:false\:false
NVIC.PriorityGroup=NVIC_PRIORITYGROUP_0
NVIC.SVCall_IRQn=true\:0\:0\:false\:false\:true\:false\:false\:false
NVIC.SysTick_IRQn=true\:0\:0\:true\:false\:true\:true\:true\:false
NVIC.TIM1_UP_TIM16_IRQn=true\:0\:0\:false\:false\:true\:true\:true\:true
NVIC.TIM2_IRQn=true\:0\:0\:false\:false\:true\:true\:true\:true
NVIC.USB_LP_CAN_RX0_IRQn=true\:0\:0\:false\:false\:true\:false\:true\:true
NVIC.UsageFault_IRQn=true\:0\:0\:false\:false\:true\:true\:false\:false
PA11.Mode=Device
PA11.Signal=USB_DM
PA12.Mode=Device
PA12.Signal=USB_DP
PA13.GPIOParameters=GPIO_Label
PA13.GPIO_Label=TMS
PA13.Locked=true
PA13.Mode=Serial_Wire
PA13.Signal=SYS_JTMS-SWDIO
PA14.GPIOParameters=GPIO_Label
PA14.GPIO_Label=TCK
PA14.Locked=true
PA14.Mode=Serial_Wire
PA14.Signal=SYS_JTCK-SWCLK
PA5.GPIOParameters=GPIO_Speed,GPIO_PuPd,GPIO_Label,GPIO_Mode
PA5.GPIO_Label=LD2 [Green Led]
PA5.GPIO_Mode=GPIO_MODE_OUTPUT_PP
PA5.GPIO_PuPd=GPIO_NOPULL
PA5.GPIO_Speed=GPIO_SPEED_FREQ_LOW
PA5.Locked=true
PA5.Signal=GPIO_Output
PB0.Locked=true
PB0.Signal=GPIO_Input
PB1.Locked=true
PB1.Signal=GPIO_Input
PB10.Locked=true
PB10.Signal=GPIO_Input
PB11.Locked=true
PB11.Signal=GPIO_Input
PB12.Locked=true
PB12.Signal=GPIO_Input
PB13.Locked=true
PB13.Signal=GPIO_Input
PB14.Locked=true
PB14.Signal=GPIO_Input
PB15.Locked=true
PB15.Signal=GPIO_Input
PB2.Locked=true
PB2.Signal=GPIO_Input
PB3.Locked=true
PB3.Signal=GPIO_Input
PB4.Locked=true
PB4.Signal=GPIO_Input
PB5.Locked=true
PB5.Signal=GPIO_Input
PB6.Locked=true
PB6.Signal=GPIO_Input
PB7.Locked=true
PB7.Signal=GPIO_Input
PB8.Locked=true
PB8.Signal=GPIO_Input
PB9.Locked=true
PB9.Signal=GPIO_Input
PC13.GPIOParameters=GPIO_Label,GPIO_ModeDefaultEXTI
PC13.GPIO_Label=B1 [Blue PushButton]
PC13.GPIO_ModeDefaultEXTI=GPIO_MODE_IT_FALLING
PC13.Locked=true
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

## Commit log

2024-10-18 Figuring out USB
    Have to use ThreadX RTOS and USBX to implement USB function. This is just the first way I got working.
2024-10-18 USB attempt
    Have to use ThreadX RTOS and USBX.
2024-10-29 Starting PCB schematics
    [AWG_FrontEnd.kicad_sch, Microcontroller.kicad_sch, Oscilloscope_FrontEnd.kicad_sch, Power_Supply.kicad_sch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]
2024-11-01 added missing GND
    [Oscilloscope_FrontEnd.kicad_sch]
2024-11-16 Starting PCB layout
    [AWG_FrontEnd.kicad_sch, Microcontroller.kicad_sch, Oscilloscope_FrontEnd.kicad_sch, Power_Supply.kicad_sch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]
2024-11-18 Finished PCB traces
    [Oscilloscope_FrontEnd.kicad_sch, USBLabTool.kicad_pcb]
2024-12-04 Update PCB
    [USBLabTool.kicad_pcb]
2025-01-06 Updated PCB Layout 1.2
    [AWG_FrontEnd.kicad_sch, Microcontroller.kicad_sch, Oscilloscope_FrontEnd.kicad_sch, Power_Supply.kicad_sch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]
2025-01-07 Revert "Updated PCB Layout 1.2"
    This reverts commit d1c1e699940df8d57e662003311594f1cc4f50c6.
    Reverting broken commit
    [AWG_FrontEnd.kicad_sch, Microcontroller.kicad_sch, Oscilloscope_FrontEnd.kicad_sch, Power_Supply.kicad_sch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]
2025-01-07 Moving files to where they should be
    [AWG_FrontEnd.kicad_sch, Microcontroller.kicad_sch, Oscilloscope_FrontEnd.kicad_sch, Power_Supply.kicad_sch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]
2025-01-15 interim update (not done)
    [AWG_FrontEnd.kicad_sch, Microcontroller.kicad_sch, Oscilloscope_FrontEnd.kicad_sch, Power_Supply.kicad_sch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]
2025-01-17 Routed revised PCB
    [AWG_FrontEnd.kicad_sch, Power_Supply.kicad_sch, USBLabTool.kicad_pcb]
2025-01-17 fix name for PWR_FLAG
    [Power_Supply.kicad_sch]
2025-02-05 update components and wiring
    [Power_Supply.kicad_sch, USBLabTool.kicad_pcb]
2025-02-11 change USB design and MCU
    [AWG_FrontEnd.kicad_sch, Microcontroller.kicad_sch, Oscilloscope_FrontEnd.kicad_sch, Power_Supply.kicad_sch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]
2025-02-16 update MCU and USB, fix some footprints
    [AWG_FrontEnd.kicad_sch, Microcontroller.kicad_sch, Oscilloscope_FrontEnd.kicad_sch, Power_Supply.kicad_sch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]
2025-02-18 modify MCU and name tags
    [AWG_FrontEnd.kicad_sch, Microcontroller.kicad_sch, Oscilloscope_FrontEnd.kicad_sch]
2025-02-19 add usb protection
    [Microcontroller.kicad_sch, USB_USER.kicad_sch]
2025-02-21 add NRST button and change MCU pins as latest
    [AWG_FrontEnd.kicad_sch, Microcontroller.kicad_sch, USB_USER.kicad_sch]
2025-02-23 Fixed up footprints
    [AWG_FrontEnd.kicad_sch, Microcontroller.kicad_sch, Oscilloscope_FrontEnd.kicad_sch, Power_Supply.kicad_sch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]
2025-02-23 Rm old libraries
    [USBLabTool.kicad_pcb]
2025-02-23 Started adding 20pin
    [Microcontroller.kicad_sch, Oscilloscope_FrontEnd.kicad_sch]
2025-02-26 add Logic Analyzer and finish pins
    Add Logic Analyzer. Add separate pins to 20 pins input(logic and scope) and 4 pins output(AWG). Add 4 programing pins.
    [AWG_FrontEnd.kicad_sch, Logic_Analyzer.kicad_pcb, Logic_Analyzer.kicad_sch, Microcontroller.kicad_sch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]
2025-02-26 minor fixes
    [AWG_FrontEnd.kicad_sch, Logic_Analyzer.kicad_sch, Microcontroller.kicad_sch, Oscilloscope_FrontEnd.kicad_sch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]
2025-02-26 footprint with minor fixes
    [Microcontroller.kicad_sch, USBLabTool.kicad_pcb, USB_USER.kicad_sch]
2025-03-01 rearrange logic pins, connectors, fix some name tags
    [Logic_Analyzer.kicad_sch, Microcontroller.kicad_sch, Oscilloscope_FrontEnd.kicad_sch, USBLabTool.kicad_pcb]
2025-03-01 Updated schematic
    [AWG_FrontEnd.kicad_sch, Microcontroller.kicad_sch, USBLabTool.kicad_pcb]
2025-03-01 Update logic analyzer schematic
    [Logic_Analyzer.kicad_sch, USBLabTool.kicad_pcb]
2025-03-01 change 3.3V regulator
    Using ST1L05APU33R instead of ST1L05CPU33R for simplicity and save of sanity
    [AWG_FrontEnd.kicad_sch, Power_Supply.kicad_sch]
2025-03-01 Updated schematic and PCB
    [AWG_FrontEnd.kicad_sch, Logic_Analyzer.kicad_sch, Microcontroller.kicad_sch, Oscilloscope_FrontEnd.kicad_sch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]
2025-03-01 update ST1L05APU33R schematic
    [Power_Supply.kicad_sch, USBLabTool.kicad_pcb]
2025-03-01 update switch name
    [Oscilloscope_FrontEnd.kicad_sch]
2025-03-01 swap MCU pins for routing
    [Microcontroller.kicad_sch, USBLabTool.kicad_pcb]
2025-03-02 starting the layout again
    [Oscilloscope_FrontEnd.kicad_sch, USBLabTool.kicad_pcb]
2025-03-05 continue PCB layout
    [AWG_FrontEnd.kicad_sch, Logic_Analyzer.kicad_sch, Microcontroller.kicad_sch, Oscilloscope_FrontEnd.kicad_sch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]
2025-03-06 Update pcb layout
    [USBLabTool.kicad_pcb]
2025-03-06 some very small wirings, and layout
    [Microcontroller.kicad_sch, USBLabTool.kicad_pcb]
2025-03-08 Updated pcb
    [USBLabTool.kicad_pcb]
2025-03-10 Updated pcb layout again
    [Oscilloscope_FrontEnd.kicad_sch, USBLabTool.kicad_pcb]
2025-03-10 Finished PCB layout
    [USBLabTool.kicad_pcb]
2025-03-11 fix the pin out
    never be lazy and stupid at the same time 👎
    [Microcontroller.kicad_sch]
2025-03-12 rearrange pins
    [Microcontroller.kicad_sch, USBLabTool.kicad_pcb]
2025-03-12 fixed the mosfet1 routing(I hope)
    route->interactive router settings
    choose highlight collisions, allow DRC violations.
    [USBLabTool.kicad_pcb]
2025-03-12 change mosfet footprint
    [USBLabTool.kicad_pcb, USB_USER.kicad_sch]
2025-03-15 fixed grounds for several components and fix 5V clean
    [AWG_FrontEnd.kicad_sch, Microcontroller.kicad_sch, Oscilloscope_FrontEnd.kicad_sch, Power_Supply.kicad_sch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]
2025-03-16 fix board wiring as mentioned in email by Prof. Kaps
    This is the follow up, wiring, of the previous schematic fix.
    [USBLabTool.kicad_pcb]
2025-03-17 final version prototype
    [Oscilloscope_FrontEnd.kicad_sch, Power_Supply.kicad_sch, USBLabTool.kicad_pcb]
2025-03-18 change scope diode footprint
    [Oscilloscope_FrontEnd.kicad_sch, USBLabTool.kicad_pcb]
2025-03-18 Added holes to PCB schematic, fixed DRC
    [Microcontroller.kicad_sch, Oscilloscope_FrontEnd.kicad_sch, USBLabTool.kicad_pcb]
2025-03-19 some more minor PCB changes
    [USBLabTool.kicad_pcb]
2025-03-19 fix footprint and change button
    [AWG_FrontEnd.kicad_sch, Microcontroller.kicad_sch, Power_Supply.kicad_sch, USBLabTool.kicad_pcb]
2025-03-20 PCB updates from meeting 3/19
    [AWG_FrontEnd.kicad_sch, Oscilloscope_FrontEnd.kicad_sch, USBLabTool.kicad_pcb, USB_USER.kicad_sch]
2025-03-20 fixed AWG pins to MCU
    [AWG_FrontEnd.kicad_sch, Microcontroller.kicad_sch, USBLabTool.kicad_pcb]
2025-03-21 just add a note
    [AWG_FrontEnd.kicad_sch]
2025-03-21 fix parameters
    [AWG_FrontEnd.kicad_sch, USBLabTool.kicad_pcb]
2025-03-22 change USB footprint, fix some warnings and problems
    [AWG_FrontEnd.kicad_sch, Microcontroller.kicad_sch, Power_Supply.kicad_sch, USBLabTool.kicad_pcb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]
2025-03-23 Resolved DRC/ERC errors in PCB and schematic
    [AWG_FrontEnd.kicad_sch, FormulaCalculator.ods, Front_EndDesign3-B_Cu_digital.gbl, Front_EndDesign3-B_Mask.gbs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]
2025-03-23 update gitignore
    [ST_LINK USB.kicad_sch]
2025-03-24 Revert 4705375 - H563 schematic is already in PCB/USBLabTool/library
    This reverts commit 4705375741c8b330ebbcd11db5d307989b1aad29.
2025-03-25 rename files
    [AWG_FrontEnd.kicad_sch, FormulaCalculator.ods, Front_EndDesign3-B_Cu_digital.gbl, Front_EndDesign3-B_Mask.gbs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]
2025-04-12 push new layout
    [AWG_FrontEnd.kicad_sch, Logic_Analyzer.kicad_sch, Microcontroller.kicad_sch, Oscilloscope_FrontEnd.kicad_sch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]
2025-04-12 pcb update
    [AWG_FrontEnd.kicad_sch, Logic_Analyzer.kicad_sch, Microcontroller.kicad_sch, Oscilloscope_FrontEnd.kicad_sch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]
2025-04-12 pcb updates
    [USBLabTool.kicad_pcb]
